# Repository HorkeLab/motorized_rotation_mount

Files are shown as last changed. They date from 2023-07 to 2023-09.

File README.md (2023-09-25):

# Description
This repository contains all files needed to convert a RSP1 rotation mount from Thorlabs (https://www.thorlabs.de/thorproduct.cfm?partnumber=RSP1/M#ad-image-0) into a motorized mount, with computer controlled rotation.

Here we provide both the 3D model, as well as .stl files of the individual parts that need to be printed.

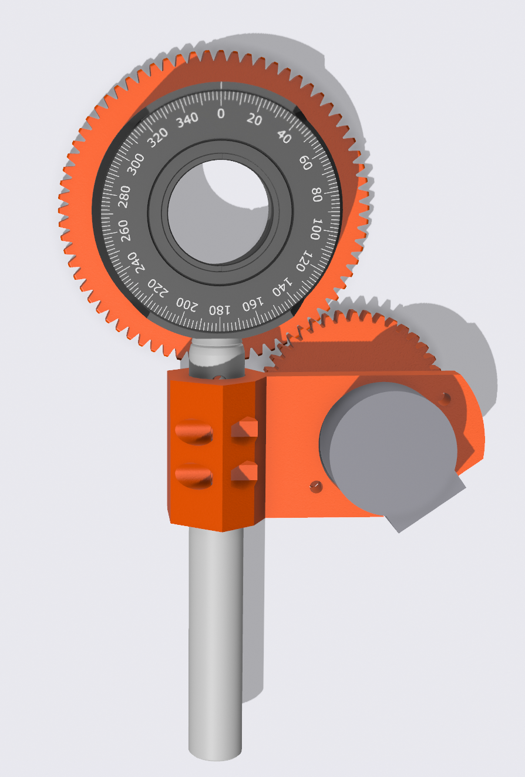
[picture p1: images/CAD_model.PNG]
CAD model of the mirror mount


Parts that need to be printed are:
- 1x Alignment tool (only needed for assembly)
- 1x Motor Mount
- 1x Mount Bracket
- 1x Cog large
- 1x Cog small

Additional parts:
- 1x 28BYJ-48 stepper motor
- 1x superglue
- M3 fasteners 

To computer control the motors we use an Arduino MEGA with sensor shield, as described here - https://github.com/HorkeLab/arduino_28BYJ-48

# Printing and assembly instructions
We have printed these in PETG, but PLA should also be fine. A well-calibrated printer is necessary to avoid excessive friction/stalling of the motors. Typically printed on 0.4mm nozzle, 0.2mm layer height, 15\% infill. You might want to print the  alignment tool slightly larger (101\% worked for us).

The large cog needs to be glued to the rotation mount. We recommend gluing it to the back side (i.e. the side that does not have the marked scale on it). It is very important that the cog is centred on the rotation mount. For this we use the alignment tool - first insert the mount into the alignment tool, apply superglue to the rotating surface, then insert the large cog (with the 'lip' facing down), as shown in the image below. Now put some heavy textbook on top and go have a coffee while the glue dries.

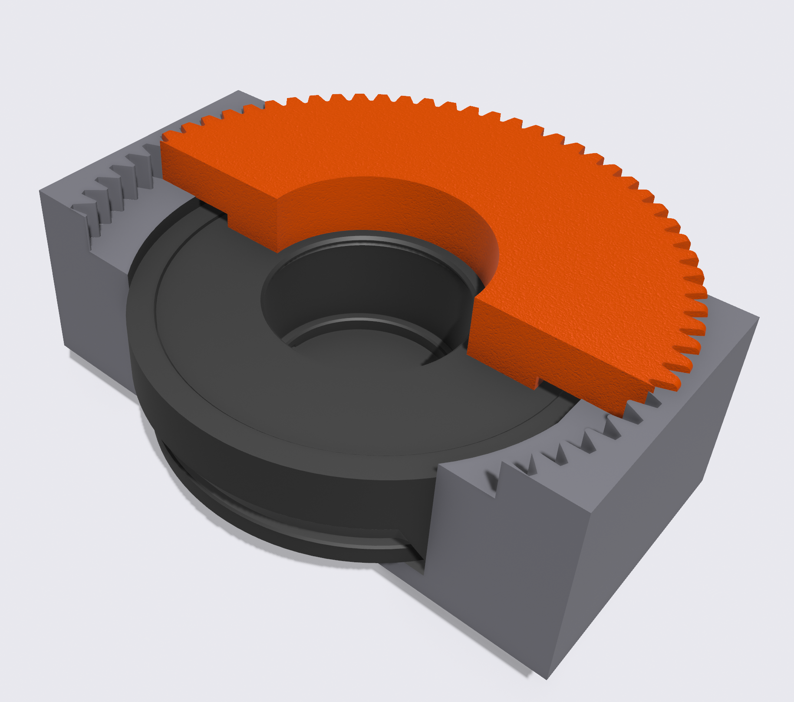
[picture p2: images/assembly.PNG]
CAD model of the alignment tool in action


The remaining assembly is fairly straightforward. Make sure the cogs are parallel to each other and well aligned. The 28BYJ-48 is quite a small low torque motor, you might have to reduce the speed to have sufficient torque to reliably rotate the mount. Some grease/oil can also help with this, and of course make sure the locking screw on the mount is not tightened.

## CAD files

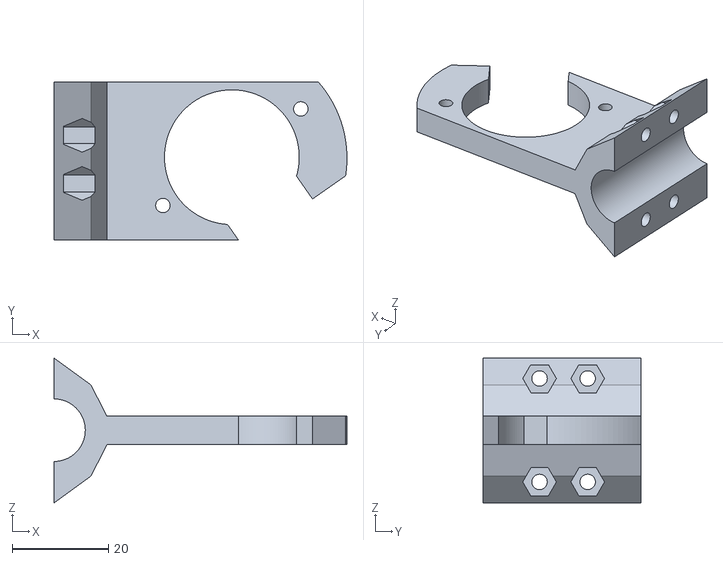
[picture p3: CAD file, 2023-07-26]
stl_files/MotorMount.stl
60.9 x 32.9 x 30.1

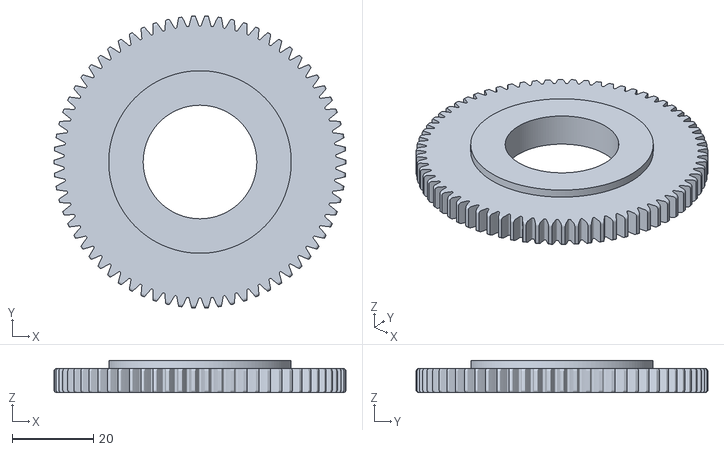
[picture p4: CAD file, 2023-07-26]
stl_files/CogLarge.stl
72.0 x 72.0 x 8.00

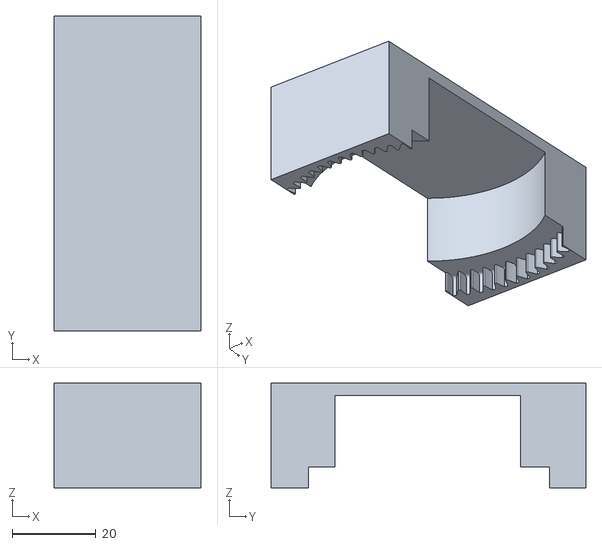
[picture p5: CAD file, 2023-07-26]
stl_files/AlignmentTool.stl
35.0 x 75.0 x 25.0

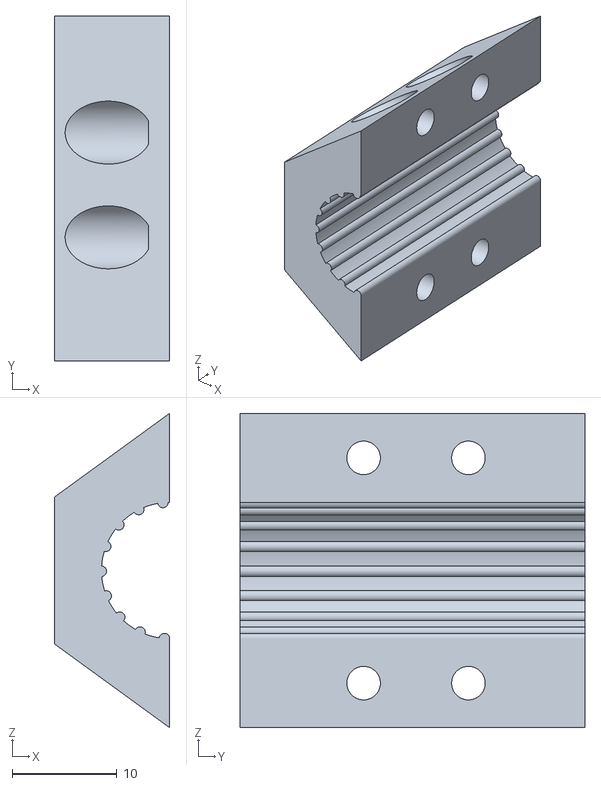
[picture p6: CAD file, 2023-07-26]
stl_files/MountBracket.stl
11.0 x 32.9 x 30.0

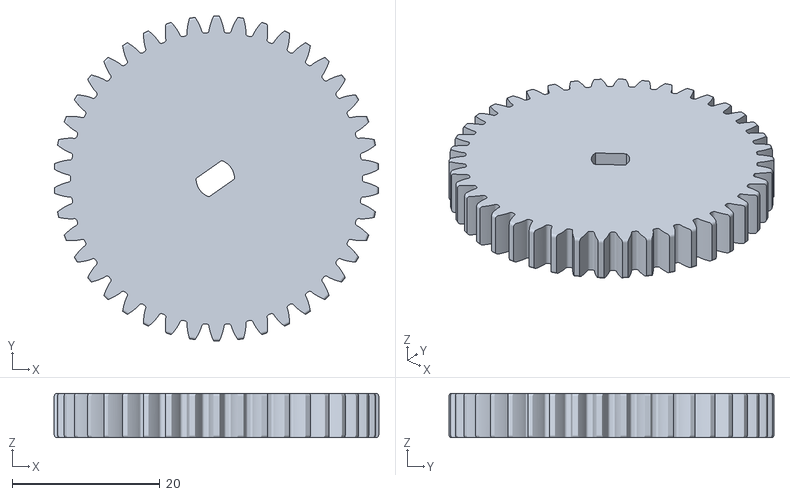
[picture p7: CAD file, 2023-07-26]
stl_files/CogSmall.stl
43.9 x 44.0 x 6.00

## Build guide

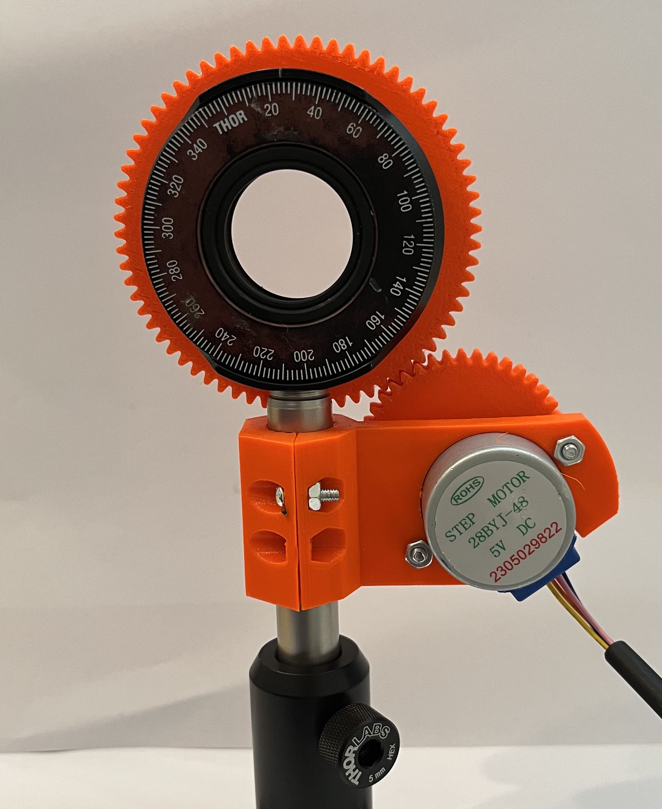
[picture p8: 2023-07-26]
images/image_assembled2.jpg

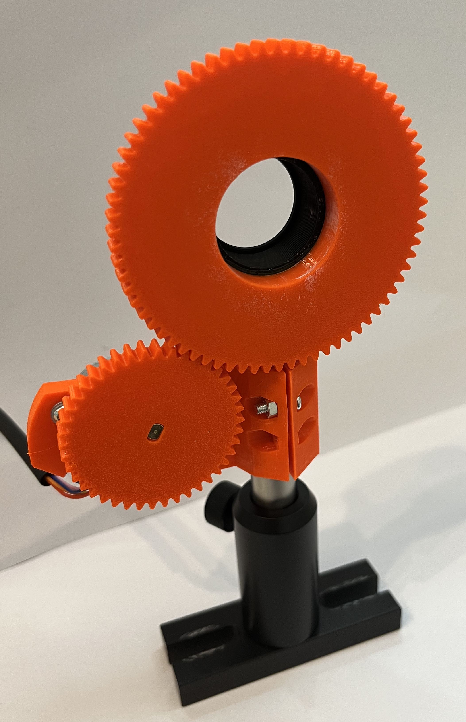
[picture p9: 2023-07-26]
images/image_assembled.jpg
